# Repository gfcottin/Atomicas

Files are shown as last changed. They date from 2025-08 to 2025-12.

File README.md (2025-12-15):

<h1 align="center">Niñas Atómicas (Atomic Girls)</h1>

<p align="center">
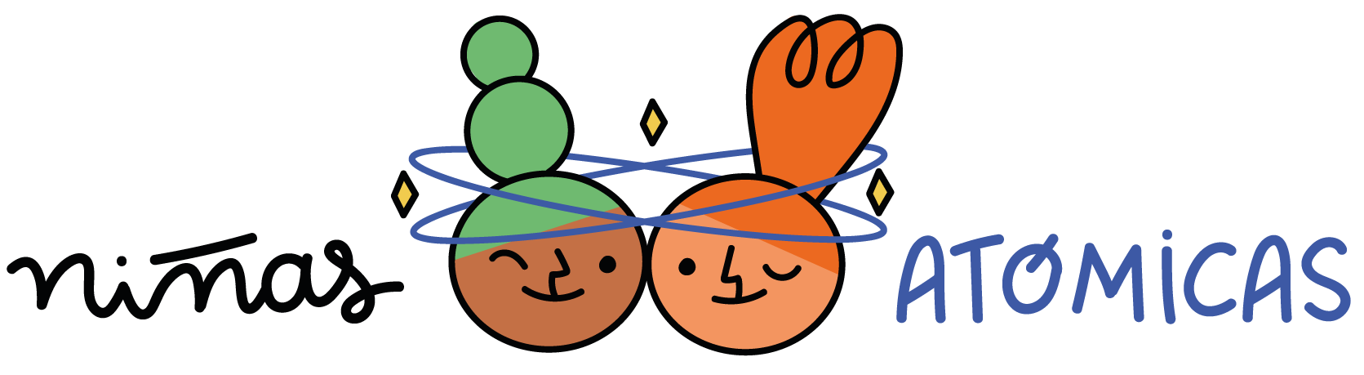
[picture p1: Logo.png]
Project Logo by Maritza Piña
  
</p>

[Niñas Atómicas](https://www.institutosaphir.cl/ninas-atomicas/) is a scientific workshop for high school girls created by Dr. Giovanna Cottin and Dr. Francisca Garay from UC Chile and SAPHIR Millenium Institute. It is designed to foster transferable scientific skills and to provide a concrete space of opportunities via hands-on experiences for girls to explore how science is done. Our workshop has run every Chilean winter since 2022.

Paper on [arXiv](https://arxiv.org/abs/2511.05754)

Owner of the [PCB](https://github.com/gfcottin/Atomicas/blob/main/PCB.png) and [Muon Counter](https://github.com/gfcottin/Atomicas/tree/main/CasingPrinter) : the Center for Theoretical and Experimental Particle Physics (CTEPP) at Universidad Andrés Bello (UNAB)

Authors of the [Detector Manual](https://github.com/gfcottin/Atomicas/blob/main/Documents/DetectorManual_Ni%C3%B1asAtomicas.pdf) (in Spanish): Devika Mukhi and Mariel Poduje. Version in [English](https://github.com/gfcottin/Atomicas/blob/main/Documents/Detector_Assembly_English.pdf) with updates from Ignacio García.

Author of the [Handbook](https://github.com/gfcottin/Atomicas/blob/main/Documents/Handbook_Ni%C3%B1asAtomicas.pdf) (in Spanish): Mariel Poduje

Designer of the Niñas Atómicas [Logo](https://github.com/gfcottin/Atomicas/blob/main/Logo.png): Maritza Piña

2025 Tutors: Florencia Díaz, Suyay Huichacura, Melanie Martínez, Daniella Mora, Devika Mukhi, Mariel Poduje, Catalina Ruiz-Tagle, Pascale Tilleria

2024 Tutors: Florencia Díaz, Suyay Huichacura, Macarena Lara, Melanie Martínez, Devika Mukhi, Mariel Poduje

2023 Tutors: Suyay Huichacura, Melanie Martínez, Devika Mukhi, Mariel Poduje, Katherine Rodriguez

2022 Tutors: Suyay Huichacura, Laura Martínez, Melanie Martínez, Devika Mukhi, Mariel Poduje

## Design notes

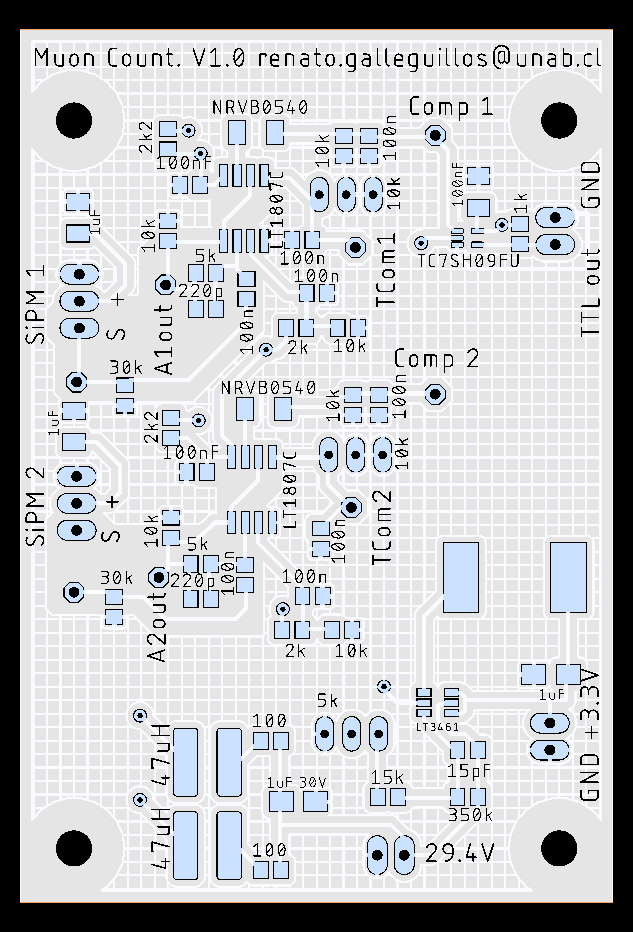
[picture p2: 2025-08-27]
PCB.png

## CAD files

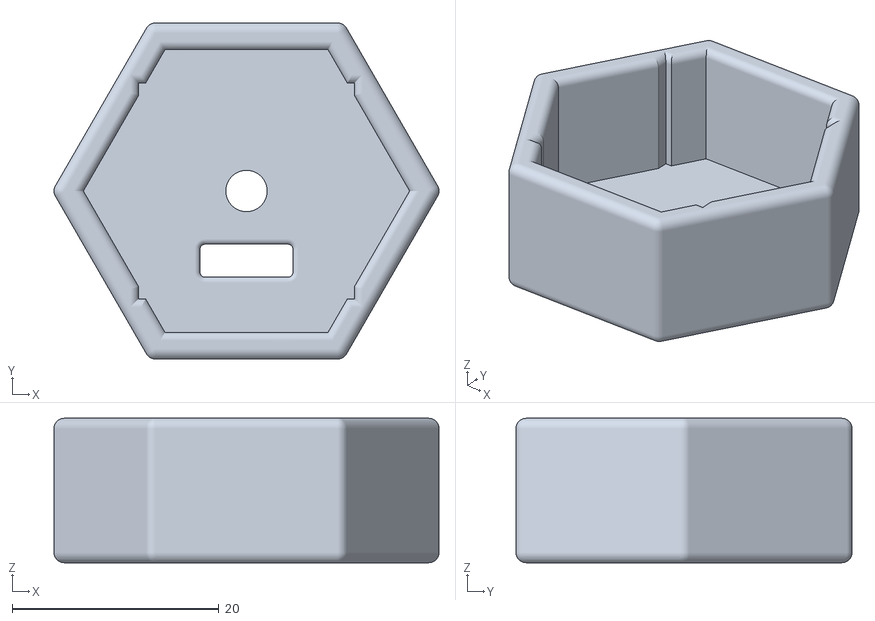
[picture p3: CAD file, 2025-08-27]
CasingPrinter/Elemento Hex.stl
37.3 x 32.6 x 14.0

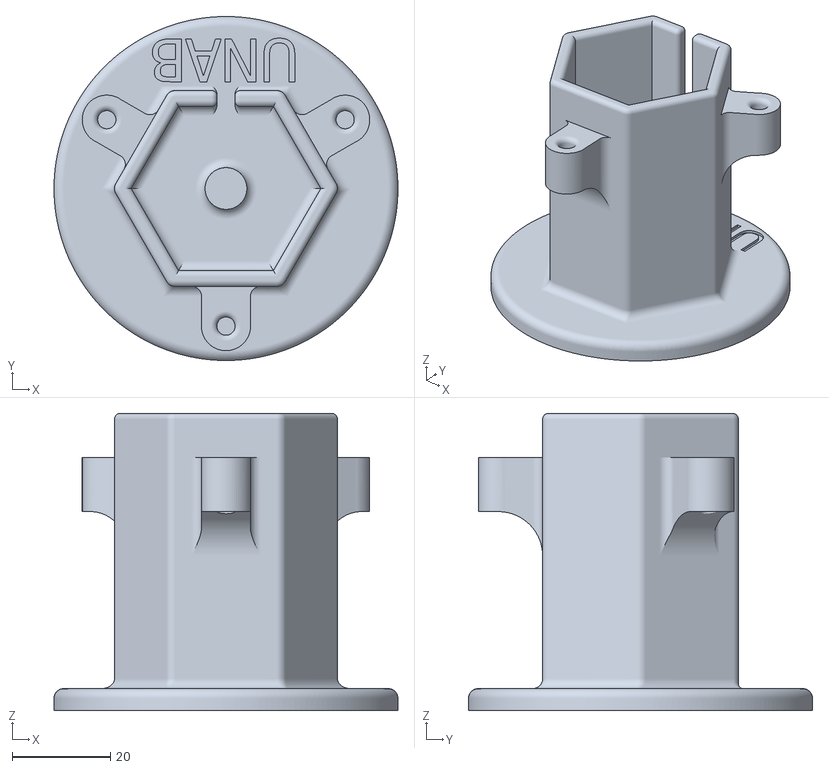
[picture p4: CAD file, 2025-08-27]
CasingPrinter/Base.stl
70.0 x 70.0 x 60.5

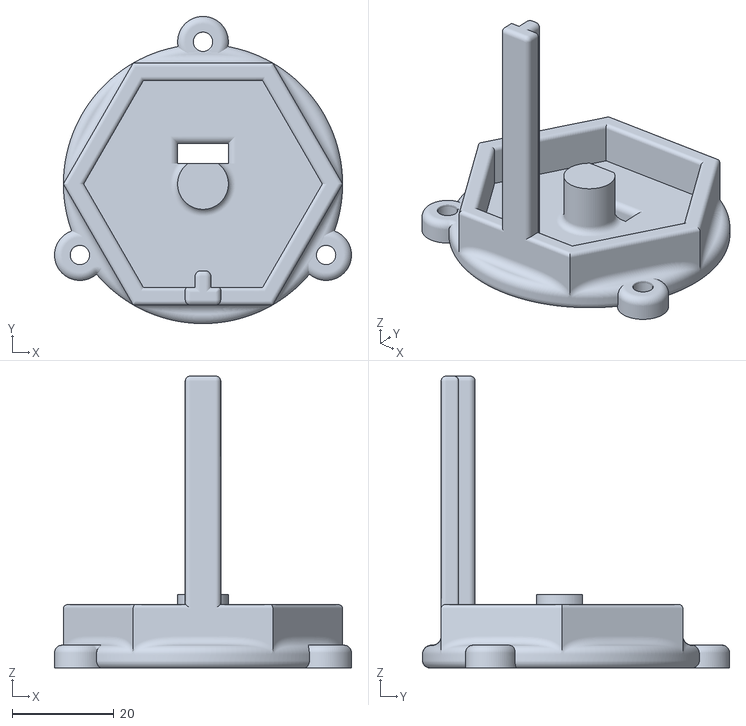
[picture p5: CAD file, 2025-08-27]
CasingPrinter/Tapa Hex.stl
58.5 x 60.5 x 57.5

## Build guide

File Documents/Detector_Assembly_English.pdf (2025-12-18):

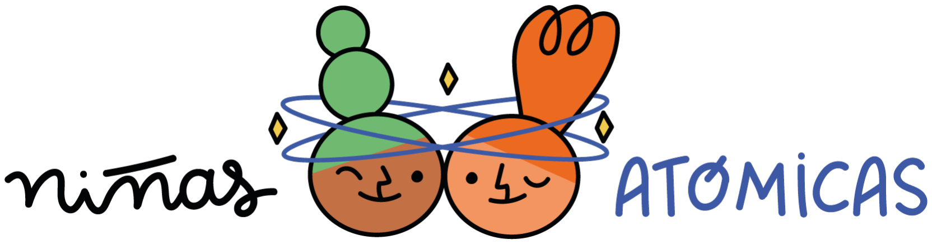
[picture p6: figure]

# “Ni˜nas At´omicas” (Atomic Girls) Hands-On Detector Assembly Instructions

Giovanna Cottin | Francisca Garay
Devika Mukhi-Nilo | Mariel Poduje | Ignacio Garc´ıa
| December 18, 2025

## Contents

1 Detector Assembly | 1
2 Electrical Connections | 4
3 Taking Data | 7

## 1 Detector Assembly

### 1.1 Materials

- Gloves
- Plastic scintillator x2
- Aluminium foil
- Teflon

1

- MicroFC-60035SMT SiPM x2
- Hexagonal casing x2
- Main detector case
- Optical grease
- Female | to | Female | Dupont
Wires x6

### 1.2 Instructions

1. Wearing gloves, wrap each plastic scintillator in aluminium foil making sure to leave exposed the side that will come in contact with the SiPM. Then, wrap the covered sides of the scintillator in Teflon.

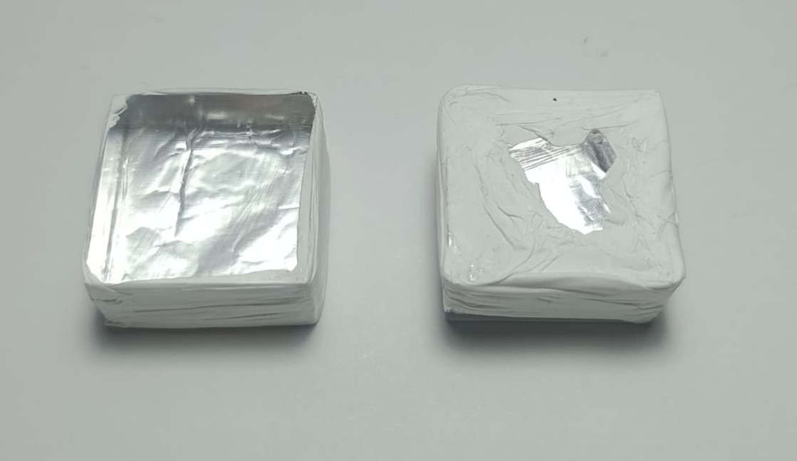
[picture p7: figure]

Figure 1: Wrapped plastic scintillator. Left scintillator shows the uncovered side.

2. Place a SiPM in each hexagonal casing of the detector. Ensure that the pins fit into the hole of the casing.

Note: When placing the SiPM, be careful not to touch or damage the silicon.

3. Apply a drop of optical grease to the silicon of the SiPM. Then place each scintillator in its respective hexagonal casing. Ensure that the exposed side of the scintillator is in contact with the SiPM.

Note: In case the scintillator must be replaced, ensure to apply another drop of optical grease to the SiPM before installing the new scintillator.

4. Connect 3 female to female dupont wires to the pins of each SiPM. Remember which wire corresponds to which pin (GND, Vin and Signal).
5. Place one array (SiPM + Scintillator + hexagonal casing + Wires) into the bottom of the detector case. The wires must pass through the slit

2

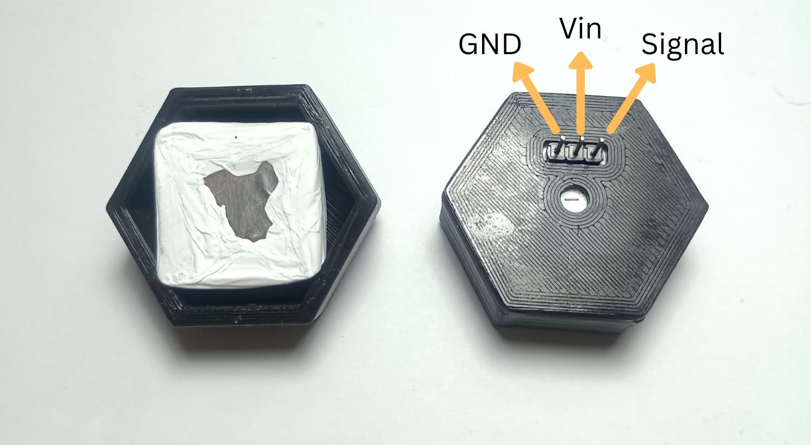
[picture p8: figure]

Figure 2: Hexagonal casing with SiPM and plastic scintillator. The uncovered side of the scintillator is in contact with the SiPM.

of the case. Ensure that the covered side of the scintillator is facing upward.

6. Place the other array into the detector case but this time with the covered side of the scintillator facing down. Both scintillators must be in contact via their covered faces in the middle of the detector case. Then place the top cover of the detector.

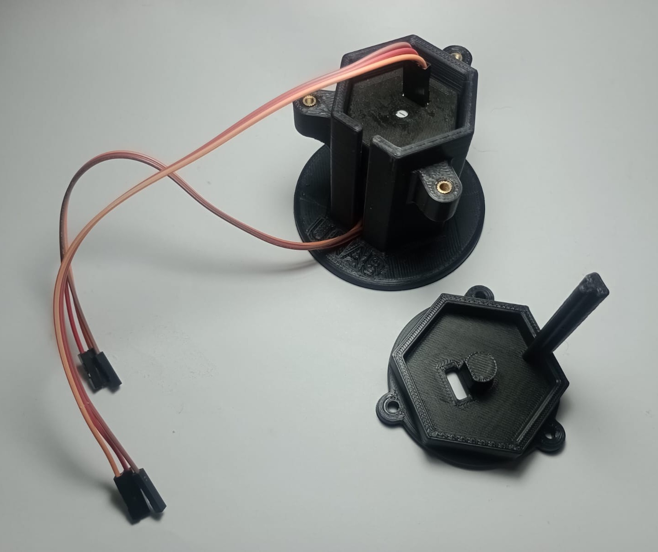
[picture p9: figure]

Figure 3: Assembled detector and its top cover.

3

## 2 Electrical Connections

### 2.1 Materials

- Muon Count PCB
- Arduino UNO
- Flathead screwdriver
- MicroSD Card Module
- MicroSD Card
- Female to Male Dupont Wires x9
- Multimeter

### 2.2 Instructions

1. Connect the 3 wires of each SiPM to the pins of the Muon Count PCB as shown in the Figure 4. Be careful to connect the Signal wire to the pin labeled S, the GND wire to the pin on the right, and the Vin wire to the “+” pin.

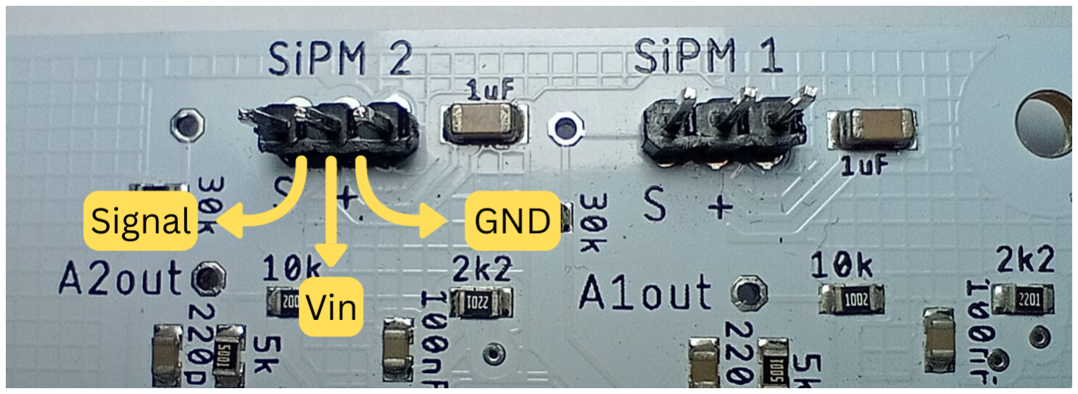
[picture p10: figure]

Figure 4: SiPM connection pins on the Muon Count PCB.

2. Connect the Muon Count PCB to the Arduino using 3 female to male dupont wires as shown in Table 1.
PCB | ARDUINO
GND | GND
3.3V | 3.3V
TTL out | D3

Table 1: Pins connections between Arduino UNO and Muon Count PCB.

Then, connect the Arduino to the power supply. This can be done by connecting the Arduino UNO to the computer with a USB cable or directly to a power socket with a transformer.

3. After connecting the Arduino UNO to the power supply, it’s necessary to calibrate the 3 potentiometers on the Muon Count PCB using a multimeter and a flathead screwdriver.

4

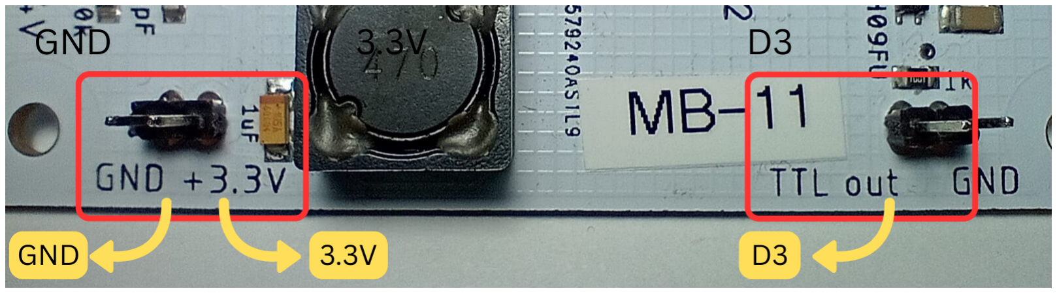
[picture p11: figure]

Figure 5: Arduino UNO connections pins on the Muon Count PCB.

a) The potentiometers (1) and (2) must be modulated so that the voltage at TCom1 and TCom2 is 2.18V. Rotate the screw clockwise to increase the voltage.
b) The potentiometer (3) must be modulated so that the voltage at the pin labeled as “29.4V” is 29.4V. Rotate the screw counterclockwise to increase the voltage.

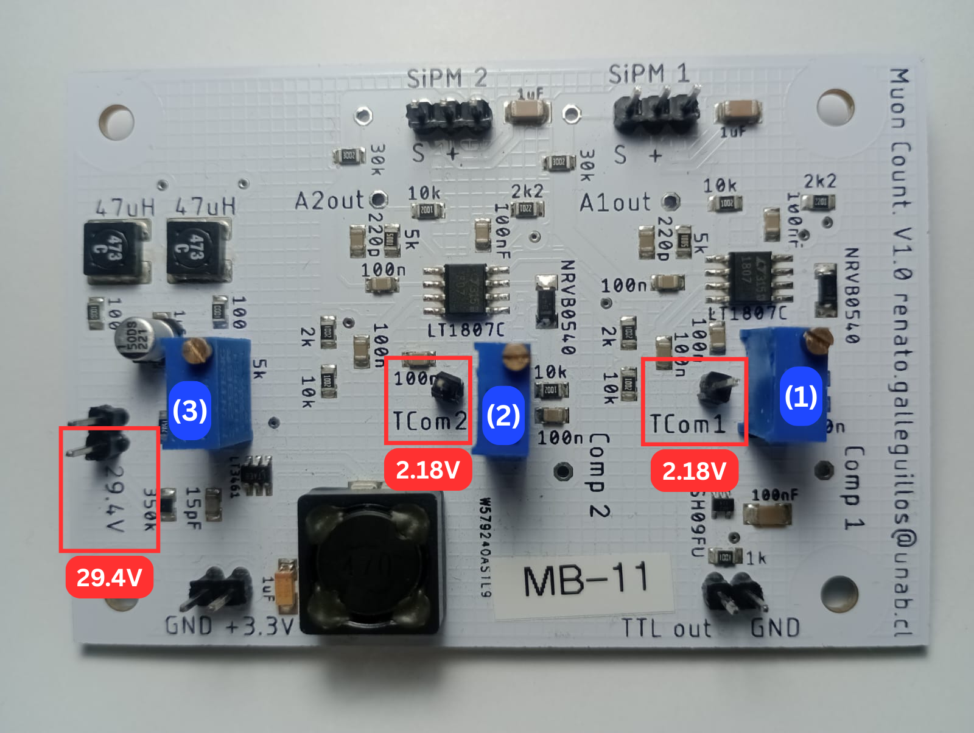
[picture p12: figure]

Figure 6: In blue: Muon Count PCB potentiometers. In red: Potentiometer voltage testing pins.

Note: At the moment of measuring the potentiometers voltages, it’s important to be careful with the connections of the measuring probes on the multimeter and to take measurements on the correct voltage scale (DC Voltage “V–”). In generics multimeters, the scale for measuring the voltage on TCom1 and TCom2 should be set to 20V, and to 200V for TCom3. See Figure 7 for reference.

4. Finally, the MicroSD Card Module must be connected to the Arduino Uno following the Table 2:

Then, connect the microSD card to the module.

Note: For the correct work of the detector it’s necessary to reset the Arduino UNO.

5

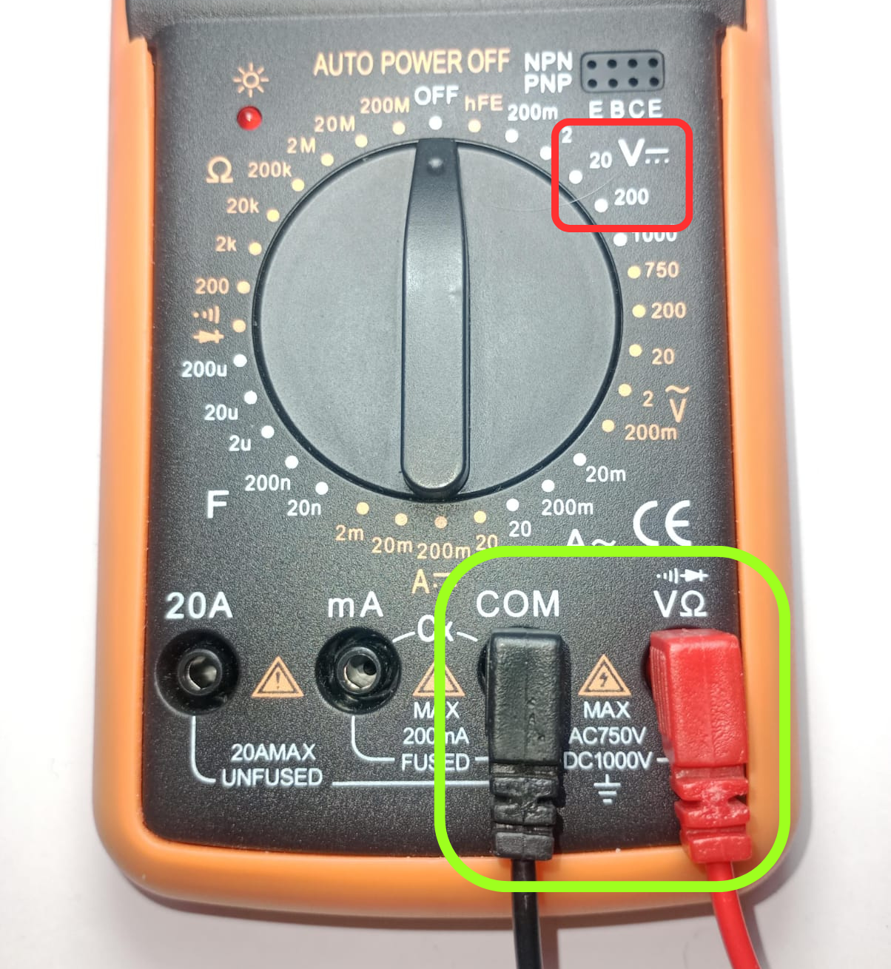
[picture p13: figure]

Figure 7: Generic Multimeter. In green: the connections of the measuring probes on the multimeter. In red: The DC voltage scales that should be used.

MicroSD Card Module | Arduino
Vcc | 5V
GND | GND
CS | D10
MOSI | D11
MISO | D12
SCK | D13

Table 2: Pins connections between MicroSD Card Module and Arduino Uno.

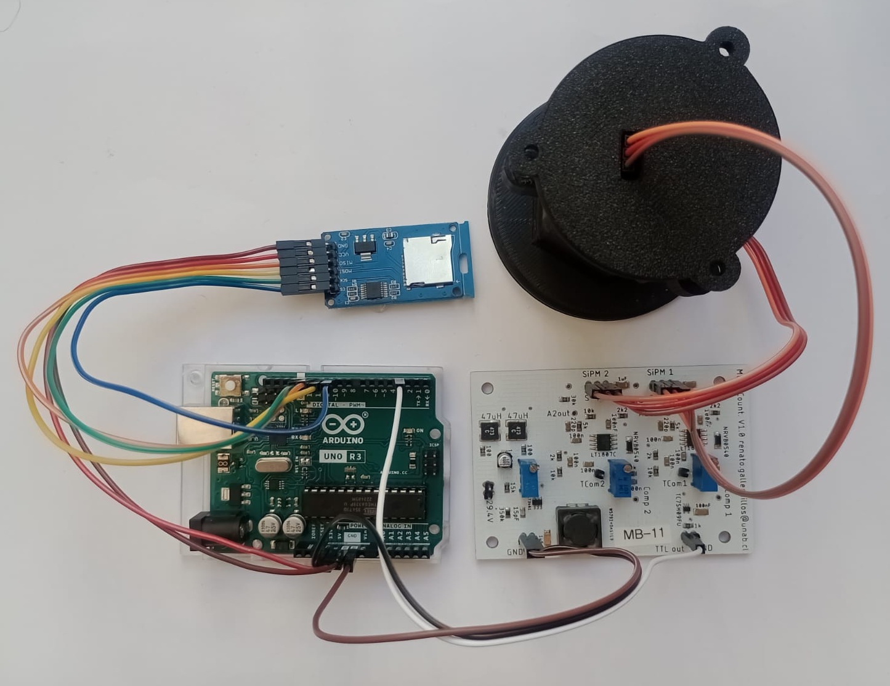
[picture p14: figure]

Figure 8: Complete Muon Detector setup.

6

## 3 Taking Data

### 3.1 Monitored Detection

The monitored detection consists in visualizing the muons passing through the detector using the serial monitor of the Arduino IDE software with a computer. If you don’t have the software, this can be downloaded for free from this LINK. (https://www.arduino.cc/en/software/)

For the monitored detection, the Arduino Uno must be connected to the computer with the Arduino IDE software. Then, open the Serial Monitor to visualize the data.

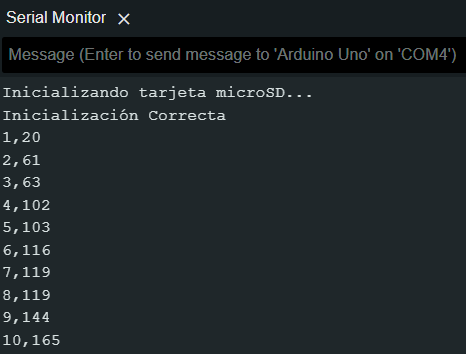
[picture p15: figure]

Figure 9: Data on Arduino IDE’s serial monitor.

The first number before the comma corresponds to the number of the detected muon, and the next number corresponds to the seconds that have elapsed since the start of the detection.

Note: Before opening the Serial Monitor, make sure to configure the board correctly in the Arduino IDE.

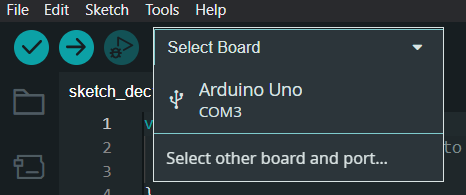
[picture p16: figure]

Figure 10: Board selection on Arduino IDE.

7

At the same time that the Serial Monitor shows the incoming muons, the data is saved to the microSD card in .txt format.

### 3.2 Unmonitored Detection

In the unmonitored detection, the Arduino Uno is not connected to the computer, but is connected to a regular power supply. In this case, real-time data cannot be viewed but it will be saved on the microSD card.

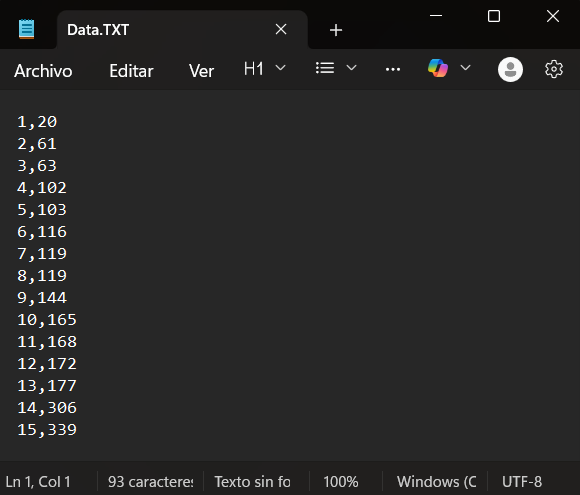
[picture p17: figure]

Figure 11: Data on .txt file.

8
